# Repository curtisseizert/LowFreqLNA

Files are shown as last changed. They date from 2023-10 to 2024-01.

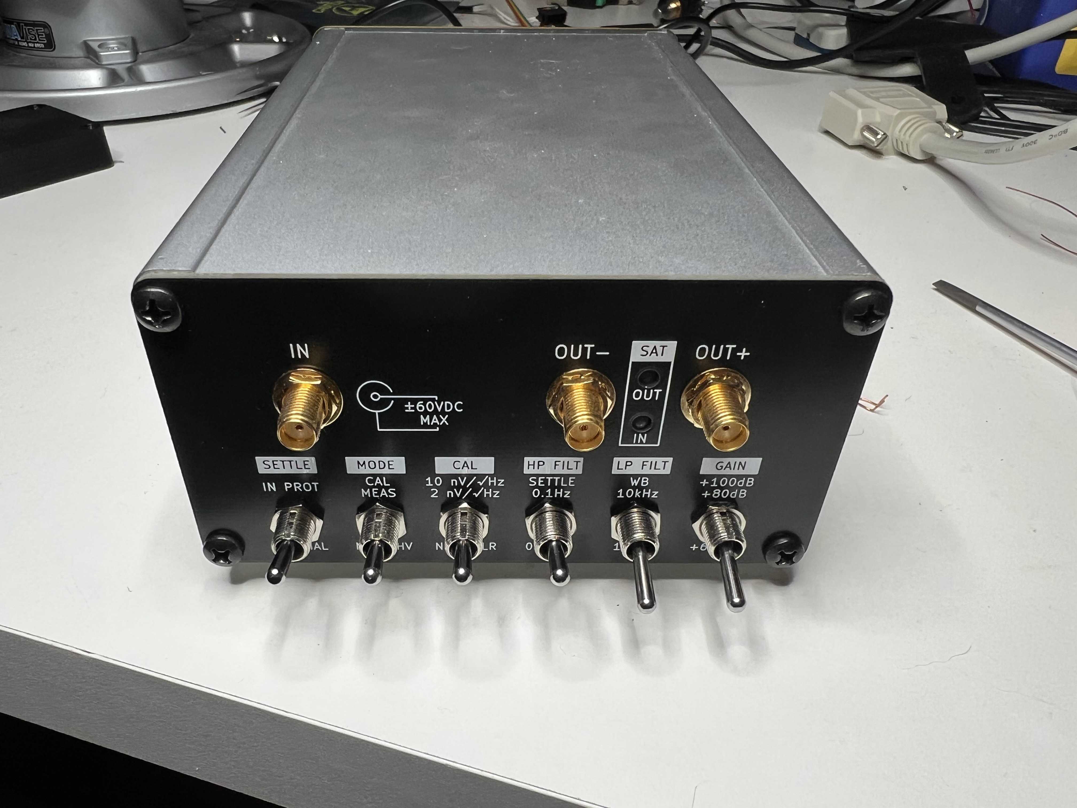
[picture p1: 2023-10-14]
Amplifier assembled.JPG

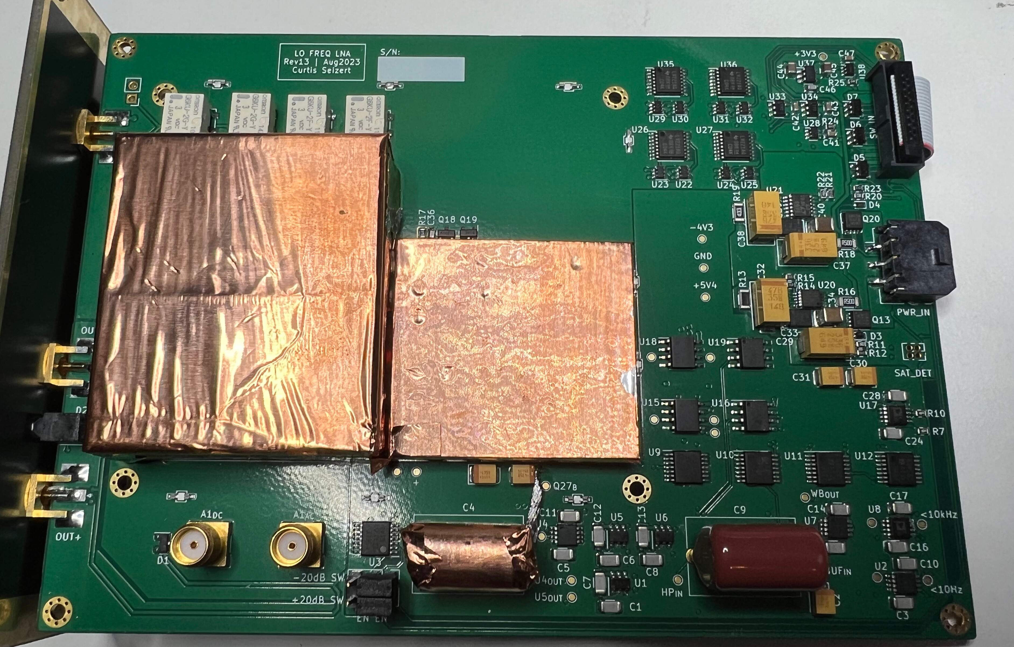
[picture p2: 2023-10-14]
Board top.jpg

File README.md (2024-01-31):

# LowFreqLNA
A 0.01Hz-1+MHz low noise amplifier

Amplifier assembled

Current Status
--------------
I have made two of these and have done a fair amount of testing to nail down root causes of some of the issues (see later in this readme) that have proven to be a bit of a nuisance. I am also moving things around a bit on the battery and battery charger boards to allow a board-to-board connection of the two and increase the clearance between the battery board and the amplifier board. I have also tested improvements to the input stage that significantly reduce the low frequency noise, lowering the 1/f corner to <1 Hz. These are detailed in the issues section #7.

1. Battery board revision: <b>complete</b>
2. Battery charger revision: <b>complete</b>
3. Low distortion buffer: back to drawing board
4. Main board revision: planning/schematic revision
5. BOM population: procrastinating

Introduction
------------

This repository contains the complete design files for a low noise AC coupled amplifier intended especially for characterization of 1/f noise of voltage references, DACs, etc. For broader applicability, it also has a reasonably high bandwidth of 2.5 MHz (measured, -3dB) at 60 or 80 dB gain, and about 1 MHz at 100 dB gain. Consistent with my primary use case for this amplifier, it has exceptionally low 1/f noise itself (measured at 3.2 nVRMS from 0.01-10 Hz) and a low broadband noise density of around 0.6 nV/rtHz. The quiescent current draw for the amplifier is about 30 mA, giving it a battery life of >100 h with the 4S 21700 Li batteries used to power the device. The project includes five PCBs:
(1) The main amplifier board
(2) The BMS board
(3) The SW board
(4) The front panel board
(5) The rear panel board/battery charger.

At present, I have hand assembled these using a converted toaster oven, which is a semi-onerous but doable-in-a-weekend task. As such, the BOMs are incomplete in all cases, which I will aim to rectify going forward. It is my hope that this will serve the needs of others designing voltage references, DACs, power supplies, etc. I may try to fix a couple things about this that have been bugging me, such as the lack of prefiltering and the antenna-like properties of the PP caps used in HP filters in the signal train. There is also a bit of room for reducing current draw. A fully differential version has been suggested, but if I work on that, I will make a separate repository for it.

The input stage is formed from a 24uF/100M RC high pass filter feeding a hybrid amplifier. The hybrid amplifier consists of 16 parallel JFE2140 dual JFETs in a cascode differential amplifier configuration. This drives an OPA140 op amp, which provides feedback via a 1k/2R divider to the inverting gate of the differential pair. The DC offset of the input stage is removed with a 2.2uF/10M HP filter. A switched gain stage amplifies the signal, which is HP filtered again to remove offsets and set the high-pass cutoff of the amplifier. The switched low-pass filtering is provided by two fourth-order butterworth filters in Sallen-Key topology. Switches select either one of these outputs or the unfiltered amplified signal to feed to the output stage.

A common problem with low-frequency AC coupled amplifiers is very long settling times when switching inputs. This is addressed with the "SETTLE" and "IN PROT" (Input protection) switches on the front panel. The former shorts the resistors of both of the post-input stage HP filter outputs with low-leakage MMBF4117 JFETs, and the latter shorts the input AC coupling filter by shorting the 100M resistor with a relay. The "IN PROT" switch also places a 6k04 resistor in series with the AC coupling filter to avoid large transients when switching between sources with different DC biases. With these switches, it is possible to take valid measurements down to 0.1 Hz with a minute or so of settling time and measurements down to 0.01 Hz with 5-10 minutes of settling time. Saturation of the amplifiers prior to both HP filters is detected with window comparators, which drive warning lights on the front panel. These features are meant to make it reasonably convenient to make low-level measurements and be confident the result is valid.

Electrical Characteristics
--------------------------

The following characteristics are taken from the one of these that I have fully assembled. Characterization was performed with a Digilent Analog Discovery Pro ADP3450 for bandwidths >10 kHz, a Keysight 34465A, and an HP3458A. Noise captures with the ADP3450 were digitized in Waveforms, exported, and transformed to the frequency domain using the SciPy Signal Python library in Spyder IDE. Captures with the HP3458A were taken using the PyVISA Python library for low frequency (50 SPS) digitization. The HP3458A was used for most low frequency work due to its superior isolation and common mode immunity. Bandwidth characterization was performed with the network analyzer utility in Waveforms for the ADP3450 and a 60dB attenuator. Gain calibration was performed by measuring the noise of a 6k04 resistor (9.97 nV/rtHz Johnson-Nyquist voltage noise density at 298k) comparing the bandwidth-limited RMS amplitude of the output signal to the theoretical value at the ambient temperature outside the amplifier. Linearity was checked by obtaining bandwidth-limited RMS amplitudes for a 240R resistor and a short, accounting for the RMS addition of the amplifier's own noise floor and that of the 240R resistor. The calibration resistors were 0.1%, 10 ppm/K thin film types. Quiescent current was measured by powering the amplifier with a Rigol DP832A DC power supply at +/-8V.

<table>
  <tr><td><b>Parameter</td><td><b>Condition</td><td><b>Result</td><td><b>Comment</td></tr>
  <tr><td>Voltage Noise Density</td><td>1 MHz</td><td>0.6 nV/rtHz</td><td>A</td></tr>
  <tr><td> </td><td>1 kHz</td><td>0.64 nV/rtHz</td><td>A</td></tr>
  <tr><td> </td><td>10 Hz</td><td>0.75 nV/rtHz</td><td>B</td></tr>
  <tr><td> </td><td>1 Hz</td><td>1.2 nV/rtHz</td><td>C</td></tr>
  <tr><td> </td><td>0.1 Hz</td><td>3.1 nV/rtHz</td><td>C</td></tr>
  <tr><td> </td><td>0.01 Hz</td><td>13.4 nV/rtHz</td><td>C,D</td></tr>
  <tr><td>Voltage Noise</td><td>0.1 Hz - 10 Hz</td><td>15 nV p-p</td><td>C</td></tr>
  <tr><td></td><td>0.01 Hz - 10 Hz</td><td>20 nV p-p</td><td>C</td></tr>
  <tr><td>Current Noise Density</td><td>0.1-1 Hz</td><td><2 fA/rtHz</td><td>E</td></tr>
  <tr><td>Input stage bias current</td><td></td><td>2.7 pA</td><td>F</td></tr>
  <tr><td>Input stage offset voltage</td><td></td><td>-94 uV</td><td>G</td></tr>
  <tr><td>-3dB Bandwidth</td><td>0R source impedance</td><td>2.8 MHz</td><td></td></tr>
  <tr><td>Input Capacitance</td><td>6k04 source impedance</td><td>140 pF</td><td>H</td></tr>
  <tr><td>10 kHz Low pass filter</td><td></td><td>4th order Butterworth</td><td></td></tr>
  <tr><td>10 Hz Low pass filter</td><td></td><td>4th order Butterworth</td><td></td></tr>
  <tr><td>THD</td><td>5 kHz</td><td><-70dB</td><td></td></tr>
  <tr><td>Quiescent Current</td><td>shorted input</td><td>30 mA</td><td></td></tr>
  <tr><td>Battery Capacity</td><td>Samsung 50S cells</td><td>5000 mA/h</td><td>nominal</td></tr>
  <tr><td>i_chg</td><td></td><td>2.7A</td><td></td></tr>
  <tr><td>Charger efficiency</td><td>V_Batt = 15V</td><td>98%</td><td>I</td></tr>
</table>

A: Full bandwidth, ADP-3450; B: 0.1-10 kHz bandwidth, ADP-3450; C: 0.01-10 Hz bandwidth, HP3458A; D: calc'd from measured value (9.5 nV/rtHz) and 3dB attenuation from HP filter; E: Calculated from open input VSD (100M resistor). Resulting noise was <0.1% from calculated value; F: Calculated from difference in offset voltage between 0R and 100M resistance to GND for input gate; G: Input gate shorted to GND; H: -3dB point with 6k04 resistor is 190 kHz. Primarily from board parasitics and RC damper; I: Measured on board, does not include cable losses

Spectra
-------

WB_Noisefloor
10kHz noisefloor loglog
10Hz noisefloor loglog
Calibration spectrum
0 1-10HzNoise
0 01-10HzNoise

Application: Measuring voltage noise of voltage references
----------------------------------------------------------
Due to the low noise floor of the preamplifier, it can be used to easily measure the voltage noise of even the quietest (room temperature) references without error due to its own noise floor. Additionally, the use of polypropylene AC coupling capacitors with low dielectric absorption and the inclusion of the "SETTLE" feature allow measurement down to 10 mHz without excessive settling time. The plot below shows the voltage noise spectral density of several ADR1000-based 10-V references. Due to the high input impedance at low frequency, increasing the source impedance does not measurably change the gain of the amplifier. This is not the case with common 1000 uF/1k AC-coupled LNAs, which give considerable gain errors at even moderate source impedances (e.g., a 100 Ohm source impedance would give a gain error of 9.1%).

ADR1000 selection VSDs

Issues
------

1. Input capacitance is higher than I'd like, which reduces the bandwidth with high impedance sources. Some of the capacitance is from board parasitics (ca. 100 pF), and some is from the R-C damper that is necessary to damp out oscillations with inductive sources (including most precision op amps). My plan to deal with this in the next revision is to modify the layout to reduce the board parasitics and switch in the R-C damper with an additional relay. Very little of the input capacitance is due to large Ciss of the paralleled JFETs as most of this presents as common mode capacitance and is bootstrapped by feedback. My target for input capacitance (with no R-C damper switched in) is 50 pF, but this is a lower priority than stability.
2. Second order (mostly) harmonic distortion of the ADA4622-2 buffer following the final HP filter stage leads to a DC offset term in the output. This is worst around 2 MHz and gets considerably worse with increasing ammplitude of the high frequency tone (it varies directly with the fourth power of the amplitude). The JFET switches are not a major issue (when SETTLE is off), which I have tested by removing them from the board. When SETTLE is on, it is worse, which negatively impacts settling time. As such, a 1 MHz sine wave amplitude modulated at 0.1 Hz will appear after 10 Hz LP filtering as a 0.1 Hz signal and harmonics, which is bad. The approach to this will be twofold: prefiltering and a composite buffer. Prefiltering will be described in #3. The composite buffer is a solution to a problem of a difficult convergence of design constraints: this buffer must have low Ib and current noise, reasonable common mode range (>+/-2.5V with 5.5V and -4.3V rails), low distortion at high frequency, and ability to operate on 10V total supply voltage with low quiescent current. To my knowledge, there are no monolithic amplifiers that satisfy these constraints. Without the high frequency distortion issue, only the ADA4622, OPAx191, and OPAx192 were good choices to my knowledge, but all of these led to the distortion-induced offset issue. In simulation, a dual JFET follower feeding an ADA4805 does well with a total quiescent current of about 1.1 mA and <0.1 dB peaking. I will prototype this block and test it before committing to the design for the next revision.
3. Amplifying signals at full bandwidth limits dynamic range for LF noise analyses. I will address this by filtering prior to the final gain stages, probably with a single-pole RC filter. Another solution would be to have the LP filter stages operate at gain >1, but I would prefer not to take this tack because it would mean the gain error of the amplifier is dependent on which LP filter stage is switched in.
4. Input protection switching is inconsistent due to contact bounce. I did not think this would be an issue with the one-shots used for relay switching, but it is. For now, connecting the K1_SW signal to both GND and 3V3 with 22k resistors does the trick, but this is not ideal, so I will implement a more robust dual-inverter debounce block for all the relay switches. In practice, however, only K1 seems to be affected by this issue due to it being switched differently on the front panel.
5. The 0804 (4x0402) resistor arrays are a PITA and almost always need to be fixed after reflow, so I'll replace those with 1206 (4x0603) arrays.
6. The 2.2 uF PP caps used in the HP filters seem to radiate, which requires shielding the input HP filter caps (these need to be PP for leakage). This shielding increases input capacitance (to ground), so I will replace the 2.2 uF caps with a few paralleled 470nF C0G capacitors, which have sufficiently low leakage to nullify the modest DC offsets following each stage, even with low frequency breakpoints.
7. The low frequency noise of the input stage is negatively impacted by the current noise of the mirror transistors. The fact that the low frequency noise is sub-optimal is evident from low frequency noise measurements of a pair of JFE2140s configured as source followers biased to the same drain current as a pair in the input stage. Because there are 16 such pairs in the LNA, the ratio of the NSD curves for this DUT and the noise floor should give a flat SNR of 12 dB, but this was not the case in the current revision. The most likely culprits to investigate were current noise from the NPN cascode transistor pair and current noise from the PNP current mirror transistor pair. Tests of the low frequency current noise of the NPN pair showed it was an unlikely culprit, accounting for perhaps 2% of the noise density at 10 mHz. Deletion of the current mirror pair, however, resolved the issue without any ill effects. This part was superfluous because the load seen by the collectors of the NPN cascode pair is the current mirror (or resistive loads) in parallel with 1/gm of the PNP folded cascode pair. With a collector current of ca. 100 uA, 1/gm is about 250R. With 330R resistive loads (i.e., shorting the collectors and emitters of the mirror transistors), the load drops from ~250R to ~142R, which still allows sufficiently high voltage gain at the emitters of the PNP pair to ensure they do not add significant noise. The effect of this modification on the low frequency noise is shown below.

JFE2140 Noise test setup

Current mirror effect on NSD

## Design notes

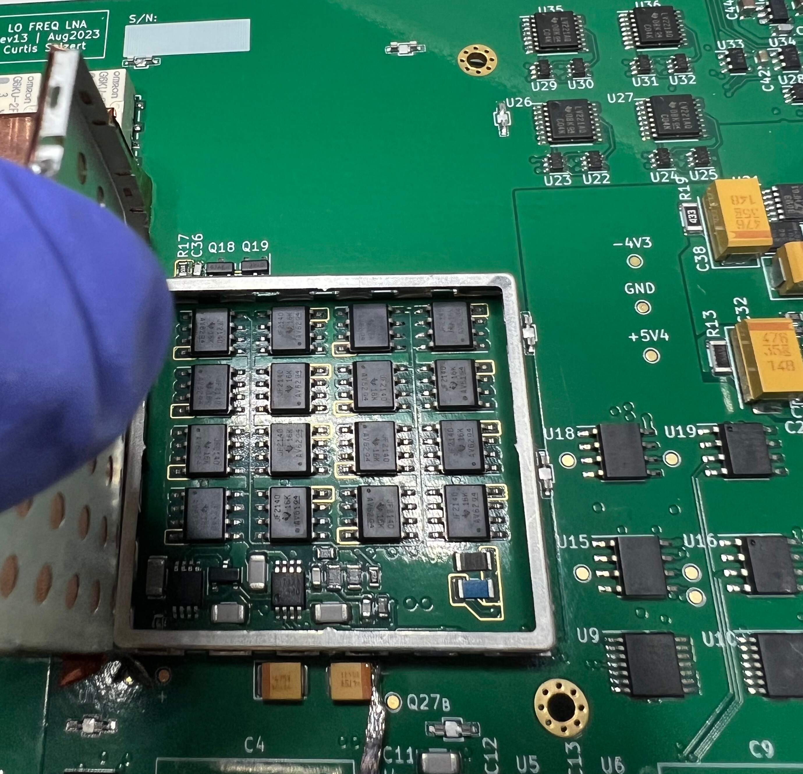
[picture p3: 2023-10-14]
Input stage.jpg

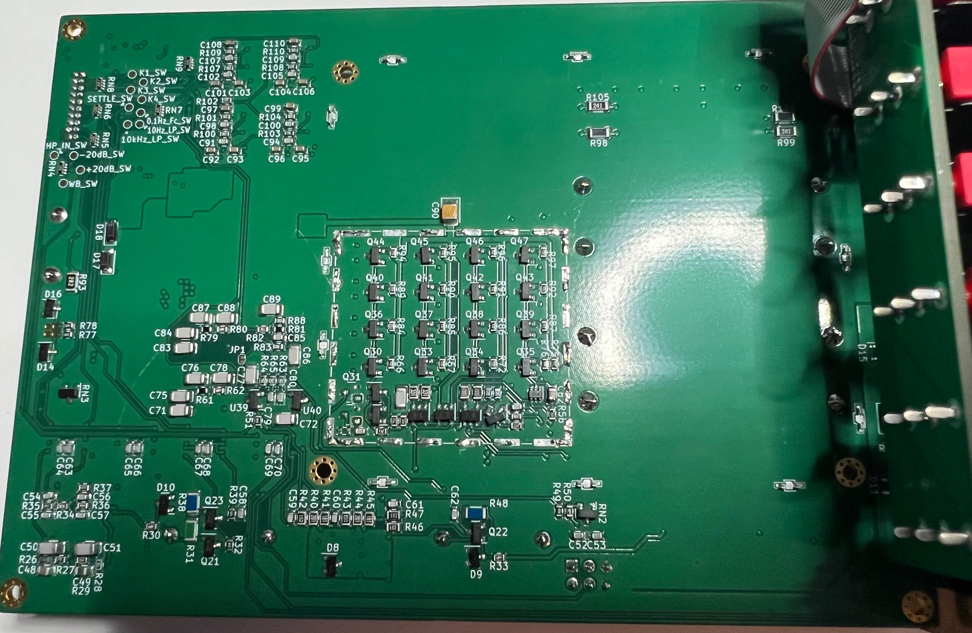
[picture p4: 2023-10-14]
Board bottom.jpg

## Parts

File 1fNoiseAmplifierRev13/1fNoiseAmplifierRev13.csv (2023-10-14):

Source: | C:\Users\Curtis\Documents\KiCAD\1fNoiseAmp\1fNoiseAmpRev12\1fNoiseAmpRev12.kicad_sch
Date: | 7/12/2023 12:35:11 AM
Tool: | Eeschema (6.0.11)
Generator: | C:\Program Files\KiCad\6.0\bin\scripting\plugins/bom_csv_grouped_by_value_with_fp.py
Component Count: | 376
Ref | Qnty | Value | Cmp name | Footprint | Description | Vendor
C1, C2, C3, C4, C5, C6, C7, C8, C11, C12, C13, C14, C16, C17, C18, C19, C20, C21, C66, C67, C84, | 21 | 100nF | C_Small | Capacitor_SMD:C_1206_3216Metric_Red | Unpolarized capacitor, small symbol
C9, C10, C15, C91, C92, | 5 | 47uF/16V | CP1_Small | Capacitor_Tantalum_SMD:CP_EIA-3528-12_Kemet-T | Polarized capacitor, small US symbol
C22, C23, C25, C26, C94, | 5 | 100nF X7R | C_Small | Capacitor_SMD:C_0603_1608Metric_red_outline | Unpolarized capacitor, small symbol
C24, C27, C28, C29, C30, C31, C32, C33, C34, C35, C36, C37, C38, C39, C40, C41, C42, C43, C44, C45, C46, C48, C49, C51, C52, C57, C64, C85, | 28 | 10nF | C_Small | Capacitor_SMD:C_0603_1608Metric_red_outline | Unpolarized capacitor, small symbol
C47, C63, | 2 | 10x470nF | C_Small | Capacitor_SMD:C_1206x10_3216Metric_Red | Unpolarized capacitor, small symbol
C50, | 1 | 33pF | C_Small | Capacitor_SMD:C_0603_1608Metric_red_outline | Unpolarized capacitor, small symbol | 81-GRM185C1H330GA01J
C53, C54, | 2 | 10pF C0G | C_Small | Capacitor_SMD:C_0603_1608Metric_red_outline | Unpolarized capacitor, small symbol
C55, C61, | 2 | 1nF | C_Small | Capacitor_SMD:C_0603_1608Metric_red_outline | Unpolarized capacitor, small symbol
C56, C62, | 2 | 47nF | C_Small | Capacitor_SMD:C_0805_2012Metric_Red_outline | Unpolarized capacitor, small symbol
C58, C65, | 2 | 470nF | C_Small | Capacitor_SMD:C_1206_3216Metric_Red | Unpolarized capacitor, small symbol
C59, C60, C78, | 3 | 10nF C0G | C_Small | Capacitor_SMD:C_0603_1608Metric_red_outline | Unpolarized capacitor, small symbol
C68, C69, | 2 | 10uF/25V | CP1_Small | Capacitor_Tantalum_SMD:CP_EIA-3528-12_Kemet-T | Polarized capacitor, small US symbol
C70, C71, | 2 | 33uF/25V | CP1_Small | Capacitor_Tantalum_SMD:CP_EIA-7343-31_Kemet-D | Polarized capacitor, small US symbol
C72, C73, | 2 | 10uF/35V | C_Small | Capacitor_SMD:C_1210_3225Metric | Unpolarized capacitor, small symbol
C74, C80, | 2 | 2.2uF X7R | C_Small | Capacitor_SMD:C_0805_2012Metric_Red_outline | Unpolarized capacitor, small symbol
C75, C76, | 2 | 22uF/50V | CP1_Small | Capacitor_Tantalum_SMD:CP_EIA-7343-31_Kemet-D | Polarized capacitor, small US symbol
C77, C79, | 2 | 10uF/25V | CP1_Small_Kelvin | Capacitor_Tantalum_SMD:CP_EIA-3528-12_Kemet-T_Kelvin | Polarized capacitor, small US symbol
C81, | 1 | 63x470nF/25V | C_Small | Capacitor_SMD:C_1206_Parallel | Unpolarized capacitor, small symbol
C82, | 1 | DNP | C_Small | Resistor_SMD:R_0603_1608Metric_red | Unpolarized capacitor, small symbol
C83, | 1 | 47nF/25V | C_Small | Capacitor_SMD:C_0805_2012Metric_Red_outline | Unpolarized capacitor, small symbol
C86, | 1 | 3.3pF C0G | C_Small | Capacitor_SMD:C_0603_1608Metric_red_outline | Unpolarized capacitor, small symbol | 81-GCM1885C2A3R3BA6D
C87, C88, C89, C90, | 4 | 100nF/50V | C_Small | Capacitor_SMD:C_1206_3216Metric_Red | Unpolarized capacitor, small symbol
C93, | 1 | 68pF C0G | C_Small | Capacitor_SMD:C_0603_1608Metric_red_outline | Unpolarized capacitor, small symbol | 81-GCM1885C2A680FA6D
D1, D2, D3, | 3 | ESDA6V1-5SC6 | ESDA6V1-5SC6 | Package_TO_SOT_SMD:SOT-23-6 | Quintuple bidirectional transil, Suppressor for ESD protection, 6V1 Breakdown, SOT-23-6
D4, D5, D6, D7, D8, D9, D10, D11, D19, D20, | 10 | DZ2S100X0L | DZ2S100X0L | Diode_SMD:D_SOD-523 | 150mW Silicon Planar Zener Diode, 10V, SOD-523 | 755-EDZVFHT2R10B
D12, D13, D14, D15, D17, D18, D22, D25, | 8 | BAV199 | BAV99 | Package_TO_SOT_SMD:SOT-23 | BAV99 High-speed switching diodes, SOT-23
D16, | 1 | LED | LED | LED_SMD:LED_Dialight_591 | Light emitting diode
D21, | 1 | BAV199DW | BAV199DW | Package_TO_SOT_SMD:SOT-363_SC-70-6 | Quad Surface Mount Low Leakage Diode, SOT-363
D23, D24, | 2 | MBR0540 | MBR0540 | Diode_SMD:D_SOD-123 | 40V 0.5A Schottky Power Rectifier Diode, SOD-123
H1, H2, H3, H4, | 4 | MountingHole_Pad | MountingHole_Pad | MountingHole:MountingHole_2.2mm_M2_Pad_Via | Mounting Hole with connection
J1, | 1 | Conn_Coaxial | Conn_Coaxial | Connector_Coaxial:SMA_Molex_73251-2120_EdgeMount_Horizontal | coaxial connector (BNC, SMA, SMB, SMC, Cinch/RCA, LEMO, ...)
J2, | 1 | Conn_01x02 | Conn_01x02 | Connector_PinHeader_2.54mm:PinHeader_1x02_P2.54mm_Vertical | Generic connector, single row, 01x02, script generated (kicad-library-utils/schlib/autogen/connector/)
J3, | 1 | IDC_HDR | Conn_02x10_Odd_Even | Connector_PinHeader_1.27mm:PinHeader_2x10_P1.27mm_Vertical | Generic connector, double row, 02x10, odd/even pin numbering scheme (row 1 odd numbers, row 2 even numbers), script generated (kicad-library-utils/schlib/autogen/connector/)
J4, | 1 | PIN_JMP | Conn_02x03_Odd_Even | Connector_PinHeader_2.54mm:PinHeader_2x03_P2.54mm_Vertical | Generic connector, double row, 02x03, odd/even pin numbering scheme (row 1 odd numbers, row 2 even numbers), script generated (kicad-library-utils/schlib/autogen/connector/)
J5, J23, | 2 | Conn_Coaxial | Conn_Coaxial | Connector_Coaxial:SMA_Molex_73251-135_SMT_Vertical | coaxial connector (BNC, SMA, SMB, SMC, Cinch/RCA, LEMO, ...)
J6, J7, J8, J9, J10, J11, J12, J13, J14, J15, J16, J17, | 12 | ShieldClip | Conn_01x01 | RF_Shielding:RF_Shield_Clip_Harwin_Mini | Generic connector, single row, 01x01, script generated (kicad-library-utils/schlib/autogen/connector/)
J18, J19, | 2 | RF_Shield_Two_Pieces | RF_Shield_Two_Pieces | RF_Shielding:Laird_Technologies_BMI-S-230-F_50.8x38.1mm | Two-piece EMI RF shielding cabinet | 739-BMI-S-230-F
J20, J21, | 2 | SMA_OUT | Conn_Coaxial | Connector_Coaxial:SMA_Molex_73251-2120_EdgeMount_Horizontal | coaxial connector (BNC, SMA, SMB, SMC, Cinch/RCA, LEMO, ...)
J22, | 1 | Micro-Fit 3.0 43650-0310 | Conn_01x03_MountingPin | Connector_Molex:Molex_Micro-Fit_3.0_43650-0310_1x03-1MP_P3.00mm_Horizontal_PnP | Generic connectable mounting pin connector, single row, 01x03, script generated (kicad-library-utils/schlib/autogen/connector/) | 538-43650-0310
K1, K2, K3, K4, | 4 | G6KU-2 | G6KU-2 | Relay_SMD:Relay_DPDT_Omron_G6K-2G-Y | Miniature 2-pole relay, Single-winding Latching | 653-G6KU-2G-Y-DC5
Q1, Q3, Q5, Q7, Q22, | 5 | BSS84 | BSS84 | Package_TO_SOT_SMD:SOT-23 | -0.13A Id, -50V Vds, P-Channel MOSFET, SOT-23
Q2, Q4, Q6, Q8, | 4 | BSS123 | BSS123 | Package_TO_SOT_SMD:SOT-23 | 0.17A Id, 100V Vds, N-Channel MOSFET, SOT-23
Q9, Q10, Q11, Q14, Q15, | 5 | MMBF4117 | MMBF4117 | Package_TO_SOT_SMD:SOT-23 | Low leakage N-Channel JFET, SOT-23
Q12, | 1 | SiS443DN | SiS443DN | Package_SO:Vishay_PowerPAK_1212-8_Single | -35A Id, -40V Vds, P-Channel MOSFET, PowerPAK 1212-8 Single
Q13, | 1 | SiS862ADN | SiS862ADN | Package_SO:Vishay_PowerPAK_1212-8_Single | 52A Id, 60V Vds, 7.2mOhm Rds(ON), N-Channel MOSFET, PowerPAK 1212-8 Single
Q16, Q17, Q20, Q24, Q27, Q29, Q31, Q33, Q35, Q37, Q39, Q41, Q43, Q45, Q47, Q49, Q51, Q53, | 18 | MMBT3904 | MMBT3904 | Package_TO_SOT_SMD:SOT-23 | 0.2A Ic, 40V Vce, Small Signal NPN Transistor, SOT-23
Q18, Q23, Q26, Q28, Q30, Q32, Q34, Q36, Q38, Q40, Q42, Q44, Q46, Q48, Q50, Q52, | 16 | JFE2140 | JFE2140 | Package_SO:SOIC-8_3.9x4.9mm_P1.27mm | Ultra-low Noise, Matched, Dual, Low-Gate Current, Discrete Audio N-Channel JFET
Q19, | 1 | HN4C51J | HN4C51J | Package_TO_SOT_SMD:SOT-23-5_red | 120V 100mA Common Base Audio Frequency GP NPN Pair
Q21, Q25, | 2 | HN4A51J | HN4A51J | Package_TO_SOT_SMD:SOT-23-5_red | 120V 100mA Common Base Audio Frequency GP PNP Pair
R1, | 1 | 6k02 0.1% | R_US | Resistor_SMD:R_1206_3216Metric_red | Resistor, US symbol | 667-ERA-8AEB6041V
R2, | 1 | 240R 0.1% | R_US | Resistor_SMD:R_1206_3216Metric_red | Resistor, US symbol | 667-ERA-8AEB241V
R3, R67, R68, | 3 | 0R5 | R_US | Resistor_SMD:R_1206_3216Metric_red | Resistor, US symbol
R4, R5, R6, R7, R8, R9, R12, R13, R14, R15, R58, | 11 | 10k | R_US | Resistor_SMD:R_0603_1608Metric_red | Resistor, US symbol
R10, R11, R16, R17, R18, R19, R20, R21, R22, R23, R63, R64, R90, R91, | 14 | 1M | R_US | Resistor_SMD:R_0603_1608Metric_red | Resistor, US symbol
R24, R25, R54, R55, R56, R59, R60, R100, R111, | 9 | 49R9 | R_US | Resistor_SMD:R_0603_1608Metric_red | Resistor, US symbol
R26, | 1 | 10M | R_US | Resistor_SMD:R_1206_3216Metric_red | Resistor, US symbol
R27, R28, R103, | 3 | 1k 0.1% | R_US | Resistor_SMD:R_0805_2012Metric_red | Resistor, US symbol
R29, | 1 | 49R9 0.1% | R_US | Resistor_SMD:R_0805_2012Metric_red | Resistor, US symbol
R30, R31, R49, R51, R86, | 5 | 1k | R_US | Resistor_SMD:R_0603_1608Metric_red | Resistor, US symbol
R32, | 1 | 47R5 | R_US | Resistor_SMD:R_0805_2012Metric_red | Resistor, US symbol | 667-ERA-6AEB47R5V
R33, | 1 | 1k24 0.1% | R_US | Resistor_SMD:R_0805_2012Metric_red | Resistor, US symbol | 71-TNPW08051K24BEEA
R34, | 1 | 240R 0.1% | R_US | Resistor_SMD:R_0805_2012Metric_red | Resistor, US symbol | 754-RG2012N-241-WT1
R35, | 1 | 220R | R_US | Resistor_SMD:R_0805_2012Metric_red | Resistor, US symbol | 667-ERA-6VEB2200V
R36, | 1 | 2k67 | R_US | Resistor_SMD:R_0603_1608Metric_red | Resistor, US symbol | 754-RR0816P-2671D42H
R37, | 1 | 56k2 | R_US | Resistor_SMD:R_0603_1608Metric_red | Resistor, US symbol | 754-RR0816P-5622D73C
R38, | 1 | 2k4 0.1% | R_US | Resistor_SMD:R_0805_2012Metric_red | Resistor, US symbol | 667-ERA-6ARW242V
R39, | 1 | 9k53 | R_US | Resistor_SMD:R_0603_1608Metric_red | Resistor, US symbol
R40, R84, | 2 | 200k | R_US | Resistor_SMD:R_0603_1608Metric_red | Resistor, US symbol | 754-RR0816P-204D
R41, | 1 | 2M87 | R_US | Resistor_SMD:R_0603_1608Metric_red | Resistor, US symbol
R42, R43, | 2 | 2M49 | R_US | Resistor_SMD:R_0603_1608Metric_red | Resistor, US symbol | 603-RC0603FR-072M49L
R44, | 1 | 1M8 | R_US | Resistor_SMD:R_0603_1608Metric_red | Resistor, US symbol | 603-AC0603FR-071M8L
R45, R97, | 2 | 887R | R_US | Resistor_SMD:R_0603_1608Metric_red | Resistor, US symbol | 754-RR0816P-8870D92A
R46, | 1 | 18k7 | R_US | Resistor_SMD:R_0603_1608Metric_red | Resistor, US symbol | 754-RR0816P-1872D27C
R47, R76, R77, R82, | 4 | 28k7 | R_US | Resistor_SMD:R_0603_1608Metric_red | Resistor, US symbol
R48, | 1 | 604k | R_US | Resistor_SMD:R_0603_1608Metric_red | Resistor, US symbol | 603-RT0603DRE07604KL
R50, R61, R62, | 3 | 100k | R_US | Resistor_SMD:R_0603_1608Metric_red | Resistor, US symbol
R52, | 1 | 499k | R_US | Resistor_SMD:R_1206_3216Metric_red | Resistor, US symbol | 667-ERA-8AEB4993V
R53, | 1 | 4M7 | R_US | Resistor_SMD:R_1206_3216Metric_red | Resistor, US symbol | 594-MCA1206MD4704BP1
R57, | 1 | 10M | R_US | Resistor_SMD:R_0603_1608Metric_red | Resistor, US symbol
R65, R66, | 2 | 2R | R_US | Resistor_SMD:R_0603_1608Metric_red | Resistor, US symbol
R69, | 1 | 43k 0.1% | R_US | Resistor_SMD:R_1206_3216Metric_red | Resistor, US symbol | 667-ERA-8AEB433V
R70, | 1 | 53k6 | R_US | Resistor_SMD:R_1206_3216Metric_red | Resistor, US symbol | 667-ERA-8AEB53R6V
R71, | 1 | 499k | R_US | Resistor_SMD:R_0603_1608Metric_red | Resistor, US symbol
R72, R74, | 2 | 30k1 | R_US | Resistor_SMD:R_0603_1608Metric_red | Resistor, US symbol
R73, | 1 | 360k | R_US | Resistor_SMD:R_0603_1608Metric_red | Resistor, US symbol | 754-RR0816P-364D
R75, | 1 | 100M | R_US | Resistor_SMD:R_1206_3216Metric_red | Resistor, US symbol | 708-HVCB1206FKC100M
R78, | 1 | 7k5 | R_US | Resistor_SMD:R_0603_1608Metric_red | Resistor, US symbol | 754-RR0816P-752D
R79, R81, R85, R89, R92, R94, R95, R96, R98, R99, R102, R105, R106, R107, R108, R109, R110, | 17 | 3k3 | R_US | Resistor_SMD:R_0603_1608Metric_red | Resistor, US symbol | 754-RR0816P-332D
R80, R83, | 2 | 330 0.1% | R_US | Resistor_SMD:R_0805_2012Metric_red | Resistor, US symbol
R87, R88, | 2 | 33k 0.1% | R_US | Resistor_SMD:R_0805_2012Metric_red | Resistor, US symbol
R93, | 1 | 100R | R_US | Resistor_SMD:R_0603_1608Metric_red | Resistor, US symbol
R101, | 1 | 4R7 | R_US | Resistor_SMD:R_0603_1608Metric_red | Resistor, US symbol | 603-RT0603FRE074R7L
R104, | 1 | 4R99 0.1% | R_US | Resistor_SMD:R_0805_2012Metric_red | Resistor, US symbol
RN1, RN2, RN3, | 3 | 33R | R_Pack04 | Resistor_SMD:R_Array_Convex_4x0402 | 4 resistor network, parallel topology
RN4, | 1 | 9k/1k | Voltage_Divider | Package_TO_SOT_SMD:SOT-23 | Voltage divider | 71-MPMT10019001AT1
RN5, RN6, | 2 | 10k/10k | Voltage_Divider | Package_TO_SOT_SMD:SOT-23 | Voltage divider
RN7, RN8, RN9, | 3 | 1M | R_Pack04 | Resistor_SMD:R_Array_Convex_4x0402 | 4 resistor network, parallel topology
TP1, TP2, TP3, TP4, TP5, TP6, TP7, TP8, TP9, TP10, TP11, TP12, TP13, TP14, TP15, TP16, TP17, TP18, TP19, TP20, TP21, TP22, TP23, TP24, TP25, TP26, TP27, TP28, TP29, TP30, TP31, | 31 | TestPoint | TestPoint | TestPoint:TestPoint_Pad_D1.0mm | test point
U1, U2, U4, | 3 | TLV1812D | TLV1812D | Package_SO:SOIC-8_3.9x4.9mm_P1.27mm | Dual Rail-to-Rail Input Comparators with Push-Pull Output, SOIC-8
U3, U7, U12, U15, U16, | 5 | DG636EEQ | DG636EEQ_4 | Package_SO:TSSOP-14_4.4x5mm_P0.65mm | 0.3 pC Charge Injection, 100 pA Leakage
U5, U21, | 2 | OPA140 | OPA140 | Package_SO:MSOP-8_3x3mm_P0.65mm | High-Precision, Low-Noise, RRO, 11 MHz JFET Op Amp
U6, U8, U10, U11, U20, | 5 | ADA4622-2 | OPA2145 | Package_SO:MSOP-8_3x3mm_P0.65mm | Dual Operational Amplifiers, DIP-8/SOIC-8/TSSOP-8/VSSOP-8
U9, U13, | 2 | ADA4807-1 | ADA4807-1 | Package_TO_SOT_SMD:SOT-23-6_red | Single Rail-to-Rail Input/Output Amplifiers, with disable, SC-70-6/SOT-23-6
U14, | 1 | TLC555xD | TLC555xD | Package_SO:SOIC-8_3.9x4.9mm_P1.27mm | Single LinCMOS Timer, 555 compatible, SOIC-8 | 700-ICM7555ISAT
U17, | 1 | LT3042xMSE | LT3042xMSE | Package_SO:MSOP-10EP-3x3_P0.5mm_EP_thermal_vias_opt | 200mA, Adjustable, Ultralow Noise, Ultrahigh PSRR RF Linear Regulator, MSOP-10
U18, | 1 | LP2985-3.3 | LP2985-3.3 | Package_TO_SOT_SMD:SOT-23-5 | 150mA 16V Low-noise Low-dropout Regulator With Shutdown, 3.3V output voltage, SOT-23-5
U19, | 1 | LT3093xMSE | LT3093xMSE | Package_SO:MSOP-12-1EP_3x4mm_P0.65mm_EP1.65x2.85mm_ThermalVias_opt | -200mA, Adjustable, Ultralow Noise, Ultrahigh PSRR RF Negative Linear Regulator, MSOP-12
U22, | 1 | 74AUP1G02 | 74AUP1G02 | Package_TO_SOT_SMD:SOT-353_SC-70-5 | Single NOR Gate, Low-Voltage CMOS | 595-SN74AUP1G02DCKT

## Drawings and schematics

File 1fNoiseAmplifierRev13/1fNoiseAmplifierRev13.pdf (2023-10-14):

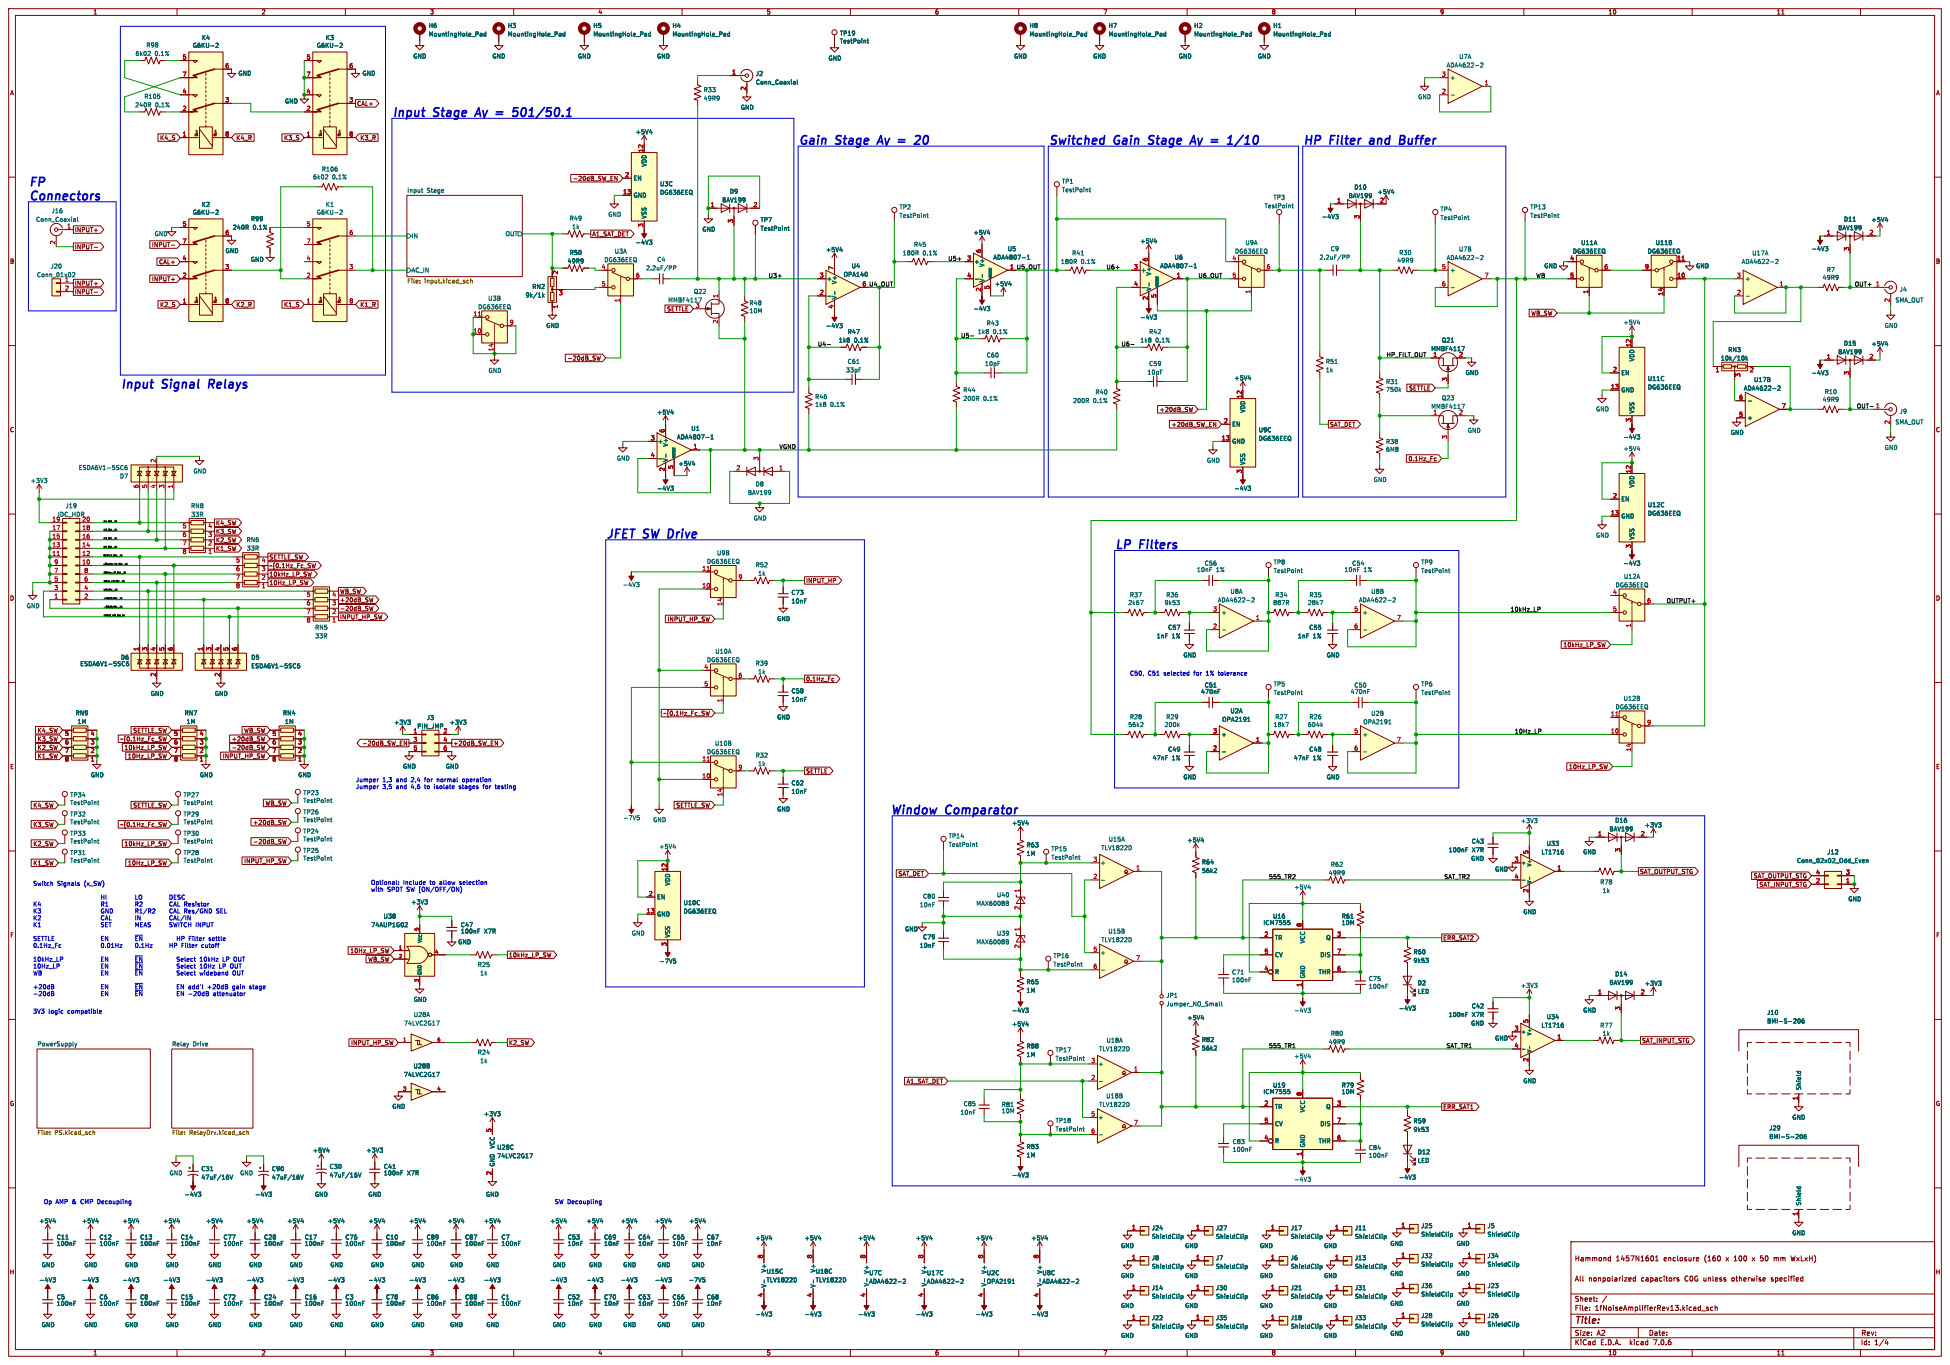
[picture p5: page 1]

HP Filter and Buffer

TP27 TestPoint TP30 TestPoint TP29 TestPoint TP28 TestPoint GND

Jumper 1,3 and 2,4 for normal operation

Jumper 3,5 and 4,6 to isolate stages for testing Switch Signals (x_SW) HI LO DESC

Op AMP & CMP Decoupling

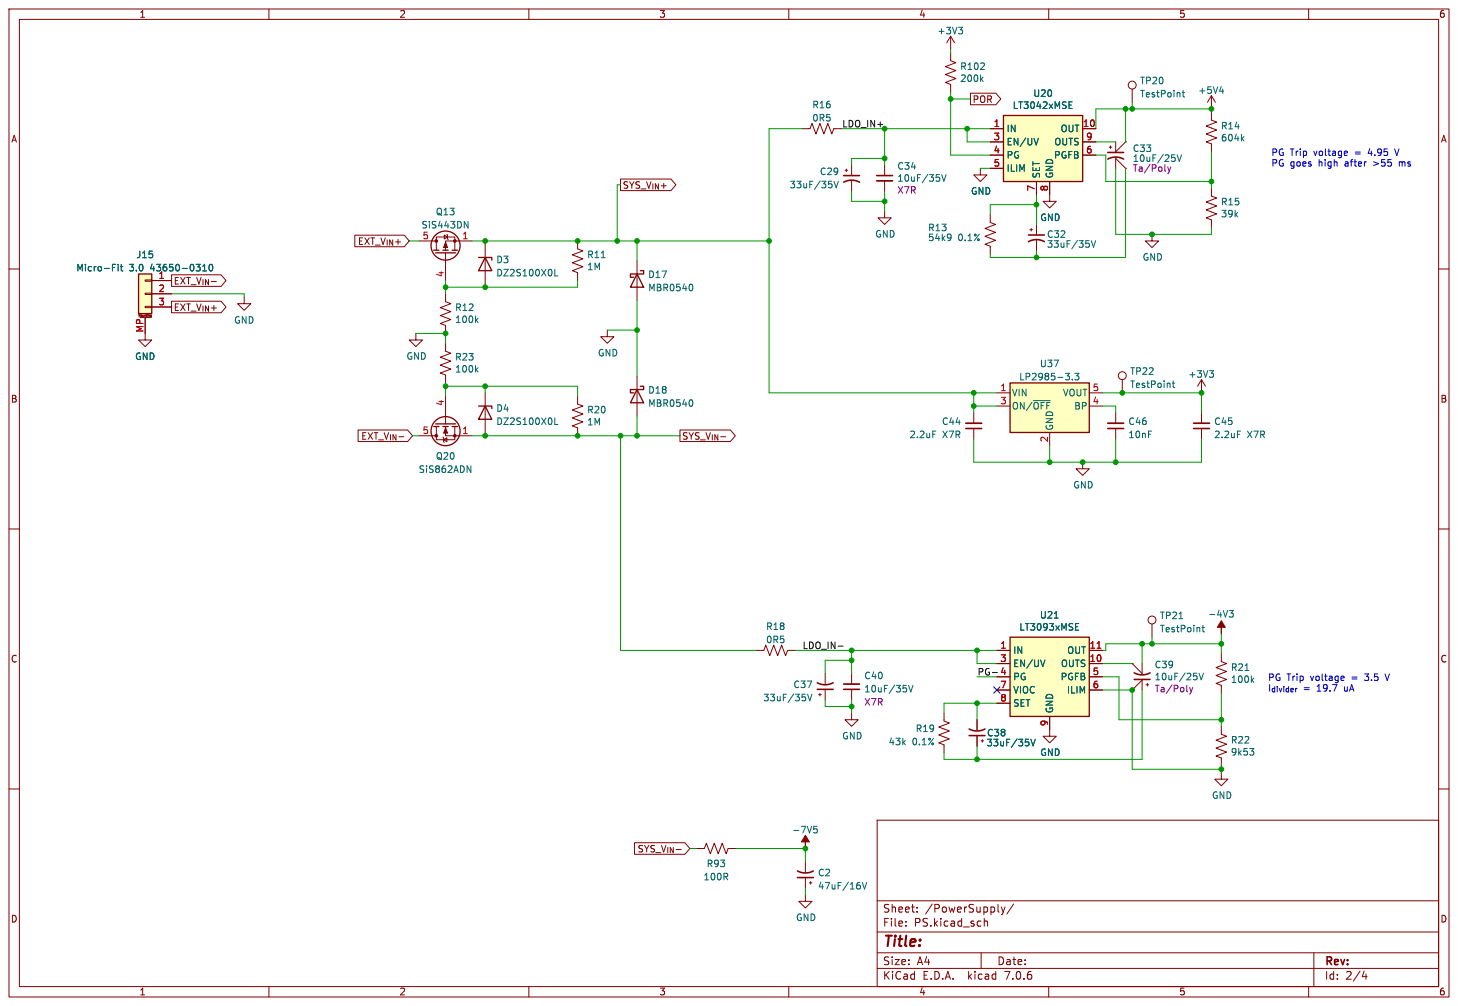
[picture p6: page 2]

PG goes high after >55 ms PG Trip voltage = 3.5 V

2 ON/~{OFF} 3 BP 4 VOUT 5 U37

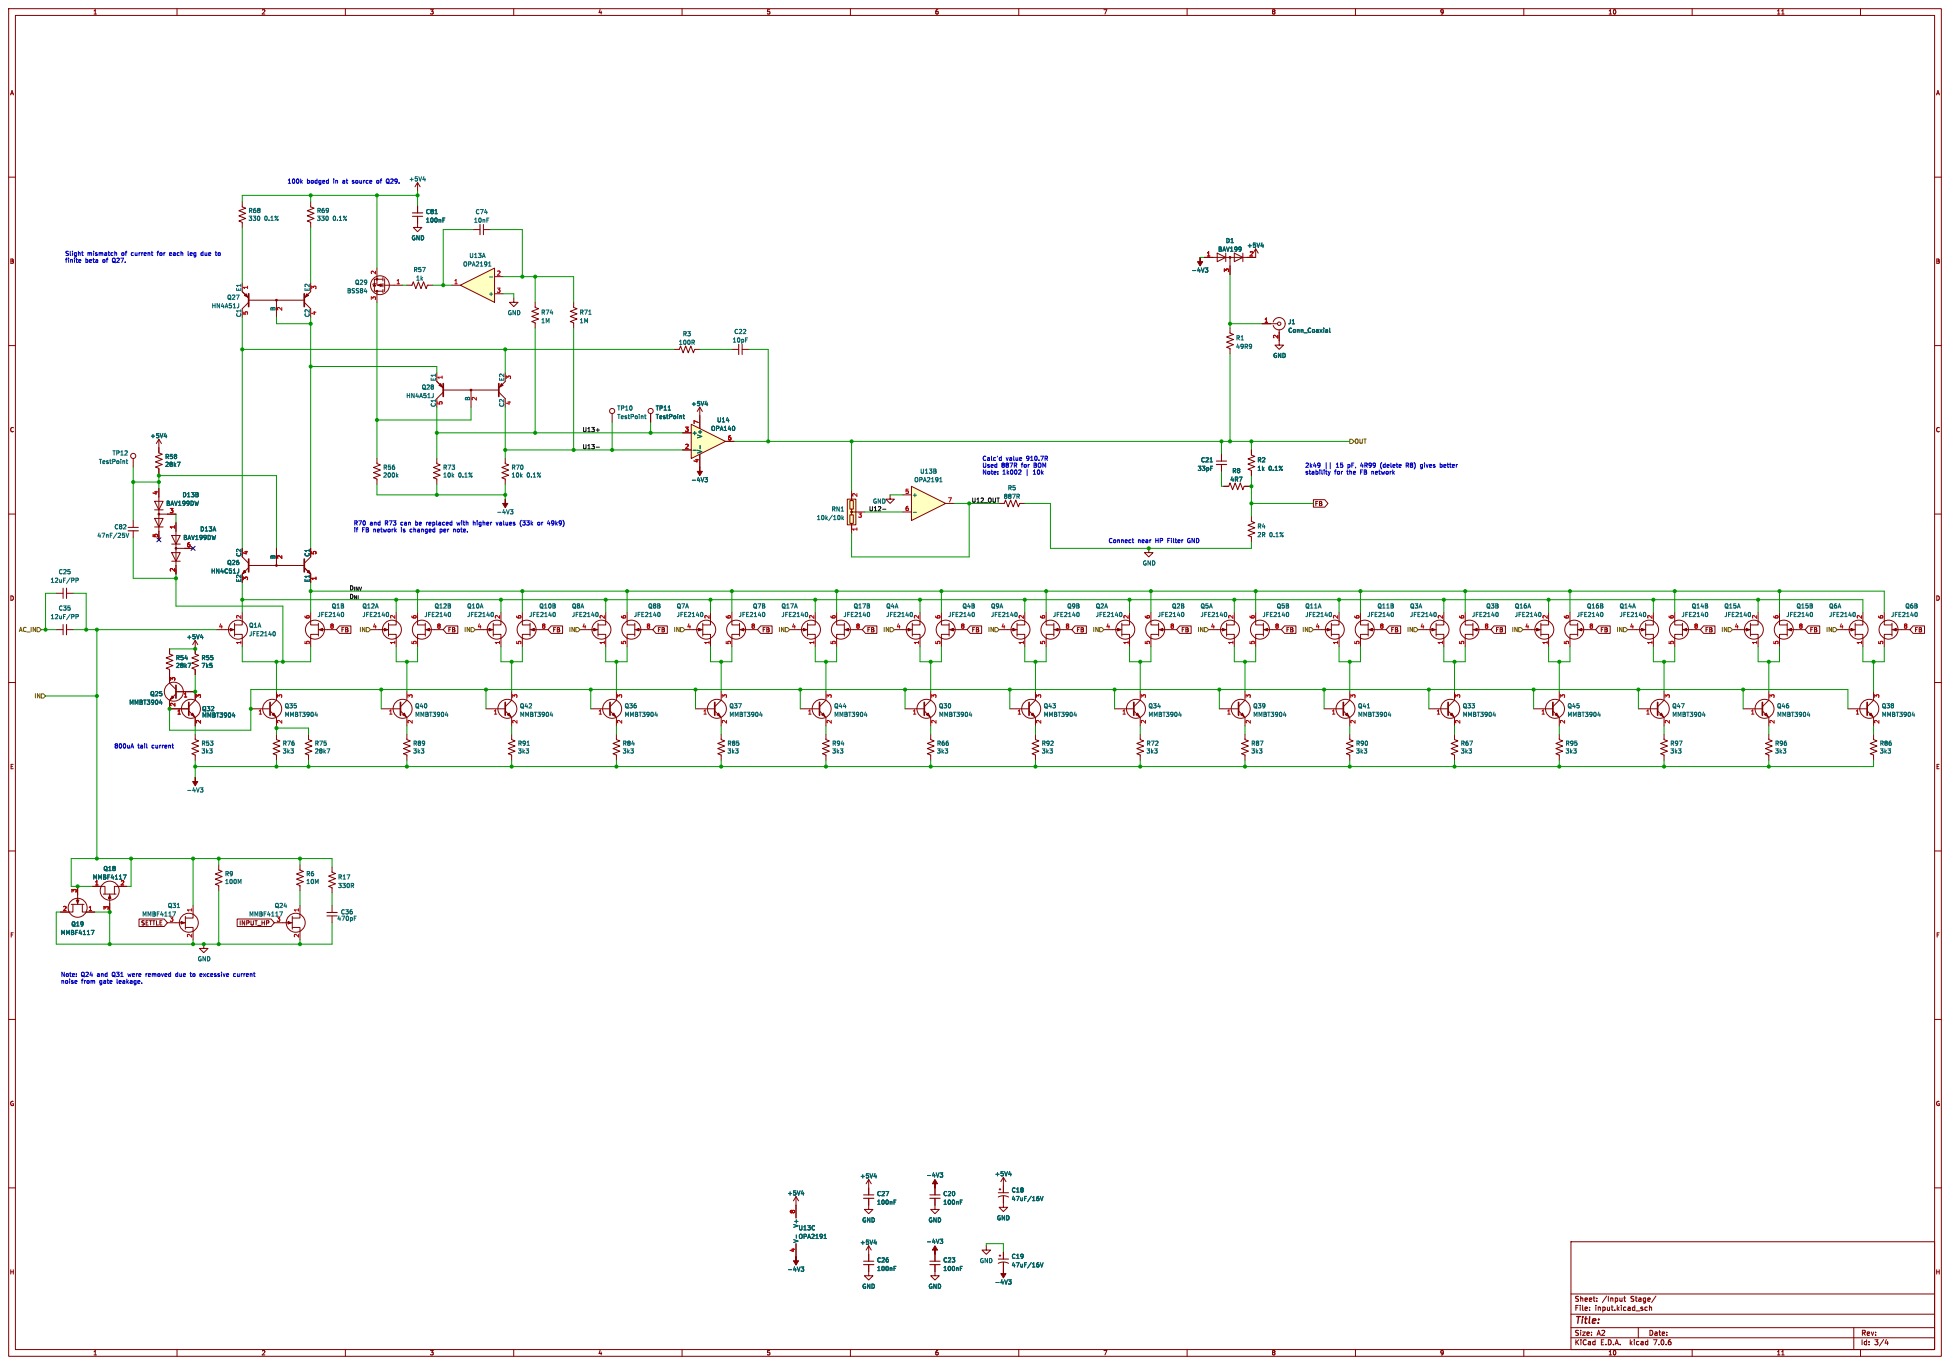
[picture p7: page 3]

if FB network is changed per note. 800uA tail current Note: Q24 and Q31 were removed due to excessive current noise from gate leakage.

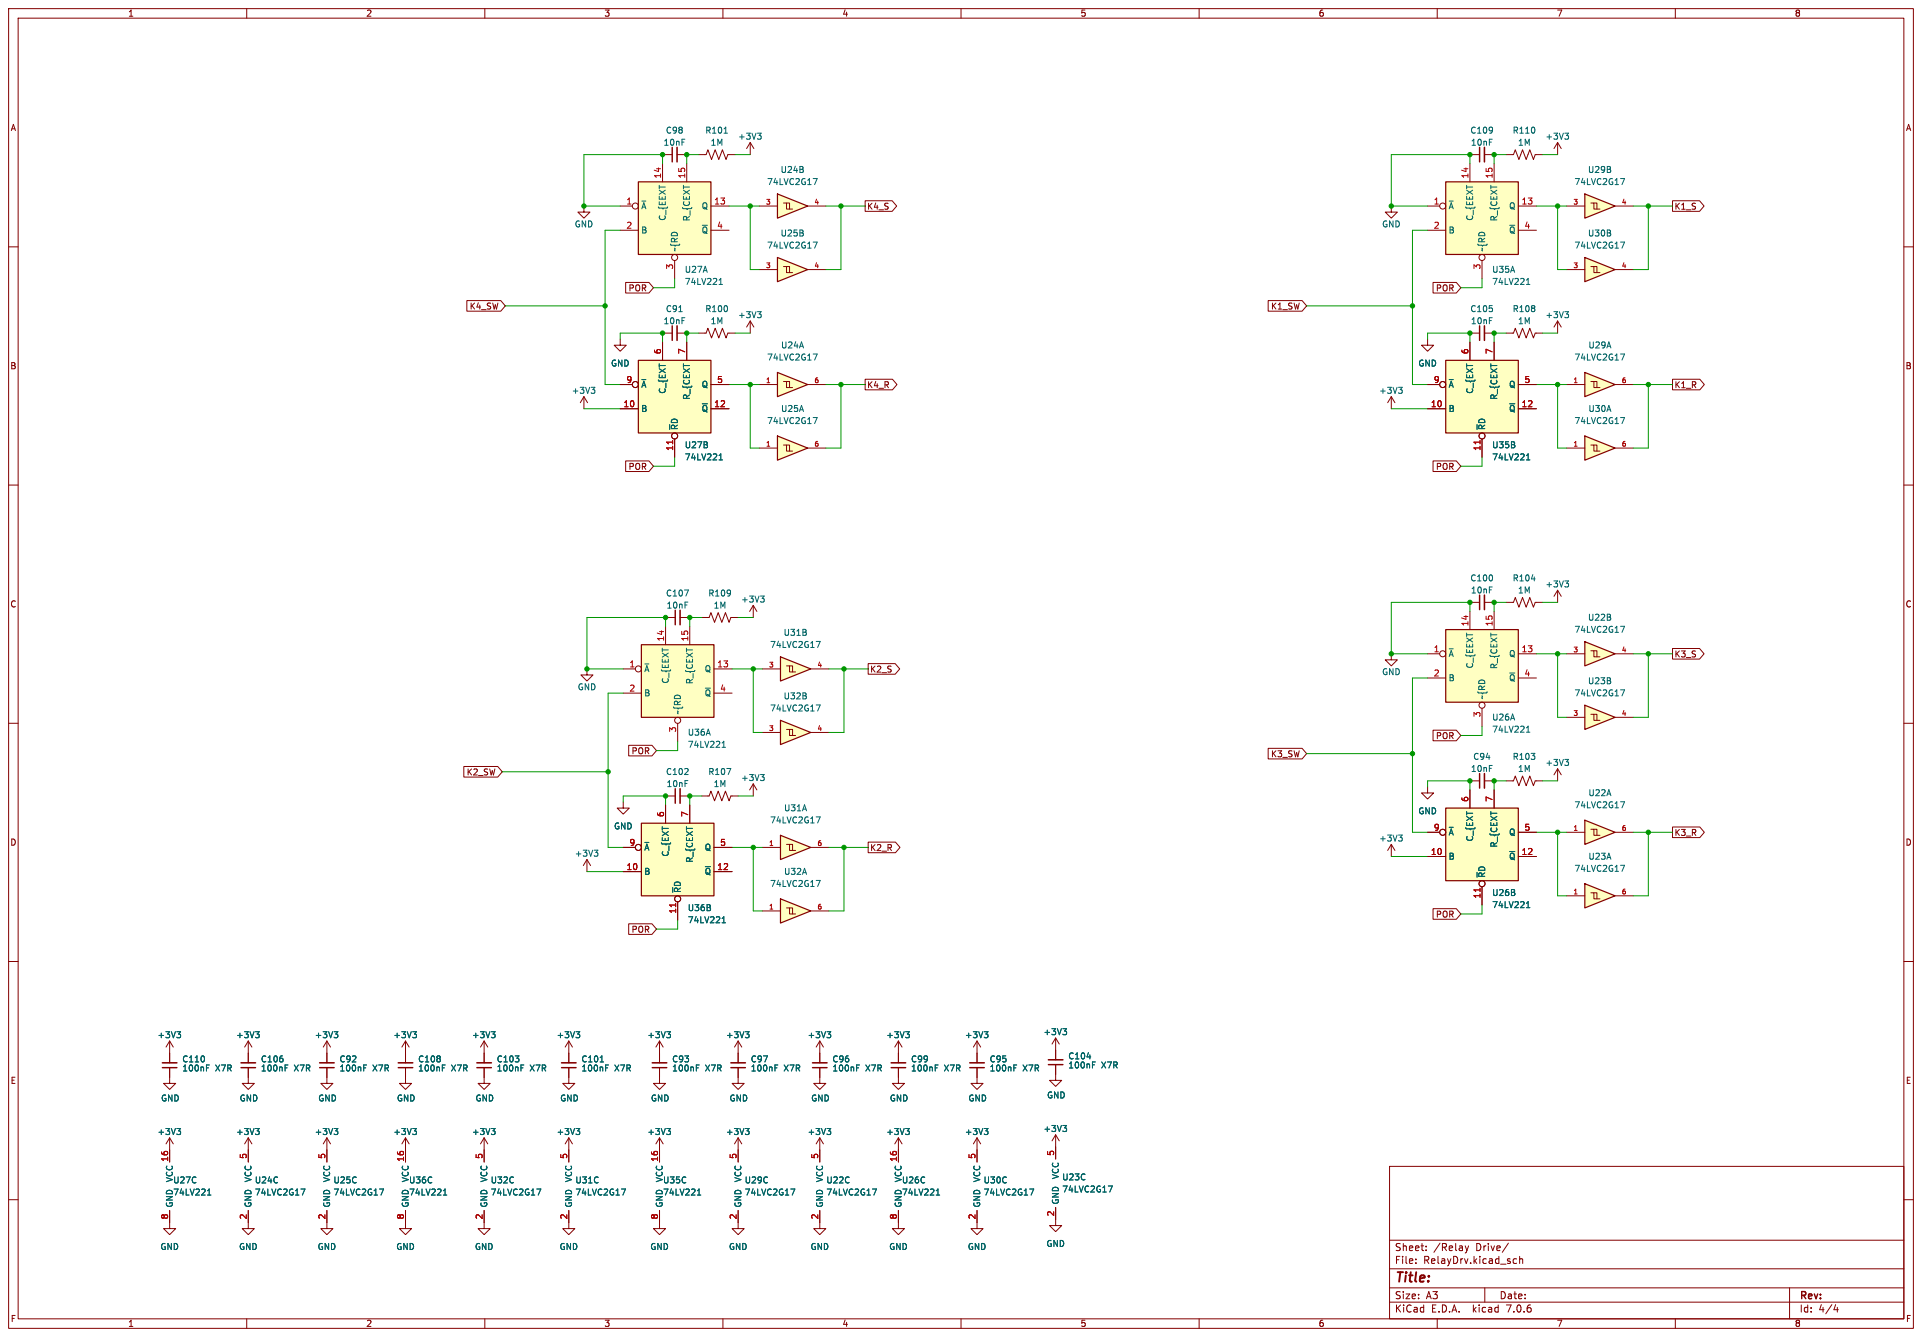
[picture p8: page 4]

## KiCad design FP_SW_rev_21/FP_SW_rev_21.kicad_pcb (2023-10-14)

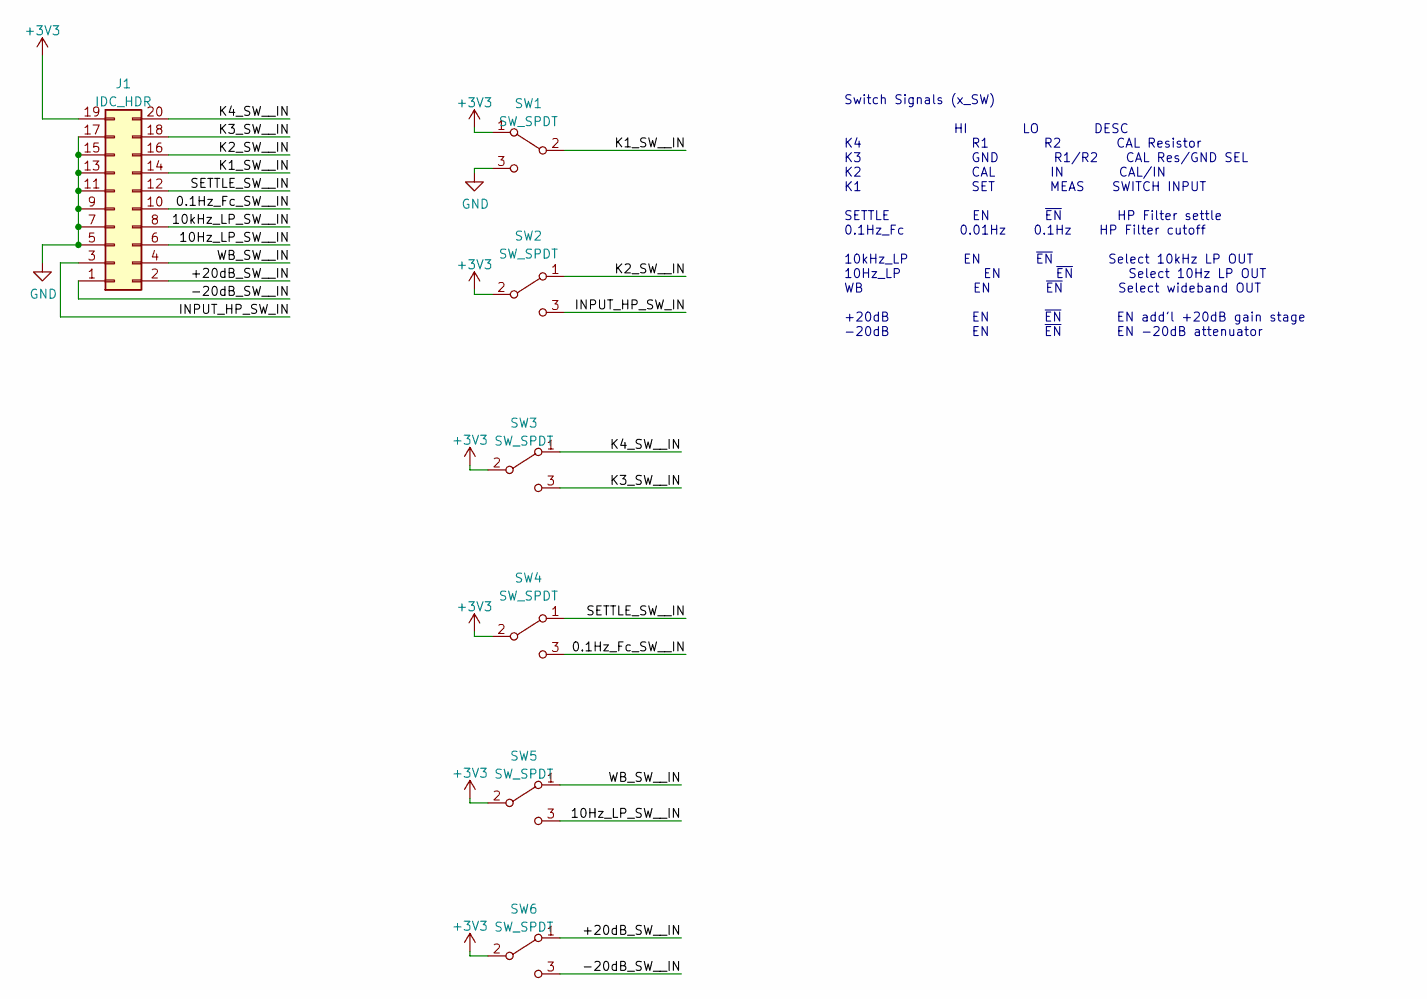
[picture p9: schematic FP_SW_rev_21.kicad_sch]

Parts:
J1: IDC_HDR; PinHeader_2x10_P1.27mm_Vertical
SW1, SW2, SW3, SW4, SW5, SW6: SW_SPDT; SW_SPDT_4.7_mm

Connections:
+3V3: J1.19, SW1.1 (A), SW2.2 (B), SW3.2 (B), SW4.2 (B), SW5.2 (B), SW6.2 (B)
/0.1Hz_Fc_SW__IN: J1.10, SW4.3 (C)
/10Hz_LP_SW__IN: J1.6, SW5.3 (C)
/10kHz_LP_SW__IN: J1.8
/+20dB_SW__IN: J1.2, SW6.1 (A)
/-20dB_SW__IN: J1.1, SW6.3 (C)
/INPUT_HP_SW_IN: J1.3, SW2.3 (C)
/K1_SW__IN: J1.14, SW1.2 (B)
/K2_SW__IN: J1.16, SW2.1 (A)
/K3_SW__IN: J1.18, SW3.3 (C)
/K4_SW__IN: J1.20, SW3.1 (A)
/SETTLE_SW__IN: J1.12, SW4.1 (A)
/WB_SW__IN: J1.4, SW5.1 (A)
GND: J1.5, J1.7, J1.9, J1.11, J1.13, J1.15, J1.17, SW1.3 (C)

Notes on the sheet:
Switch Signals (x_SW) HI LO DESC K4 R1 R2 CAL Resistor K3 GND R1/R2 CAL Res/GND SEL K2 CAL IN CAL/IN K1 SET MEAS SWITCH INPUT SETTLE EN ~{EN} HP Filter settle 0.1Hz_Fc 0.01Hz 0.1Hz HP Filter cutoff 10kHz_LP EN ~{EN} Select 10kHz LP OUT 10Hz_LP EN ~{EN} Select 10Hz LP OUT WB EN ~{EN} Select wideband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

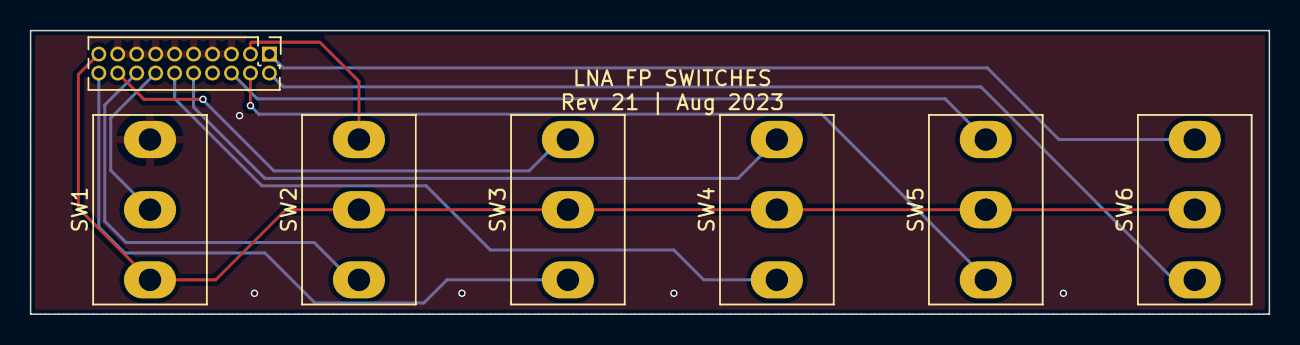
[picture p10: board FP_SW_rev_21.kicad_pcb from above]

Board: 2 copper layers, 83.0 x 19.0 mm, 7 parts (0 on the bottom side), 13 nets.

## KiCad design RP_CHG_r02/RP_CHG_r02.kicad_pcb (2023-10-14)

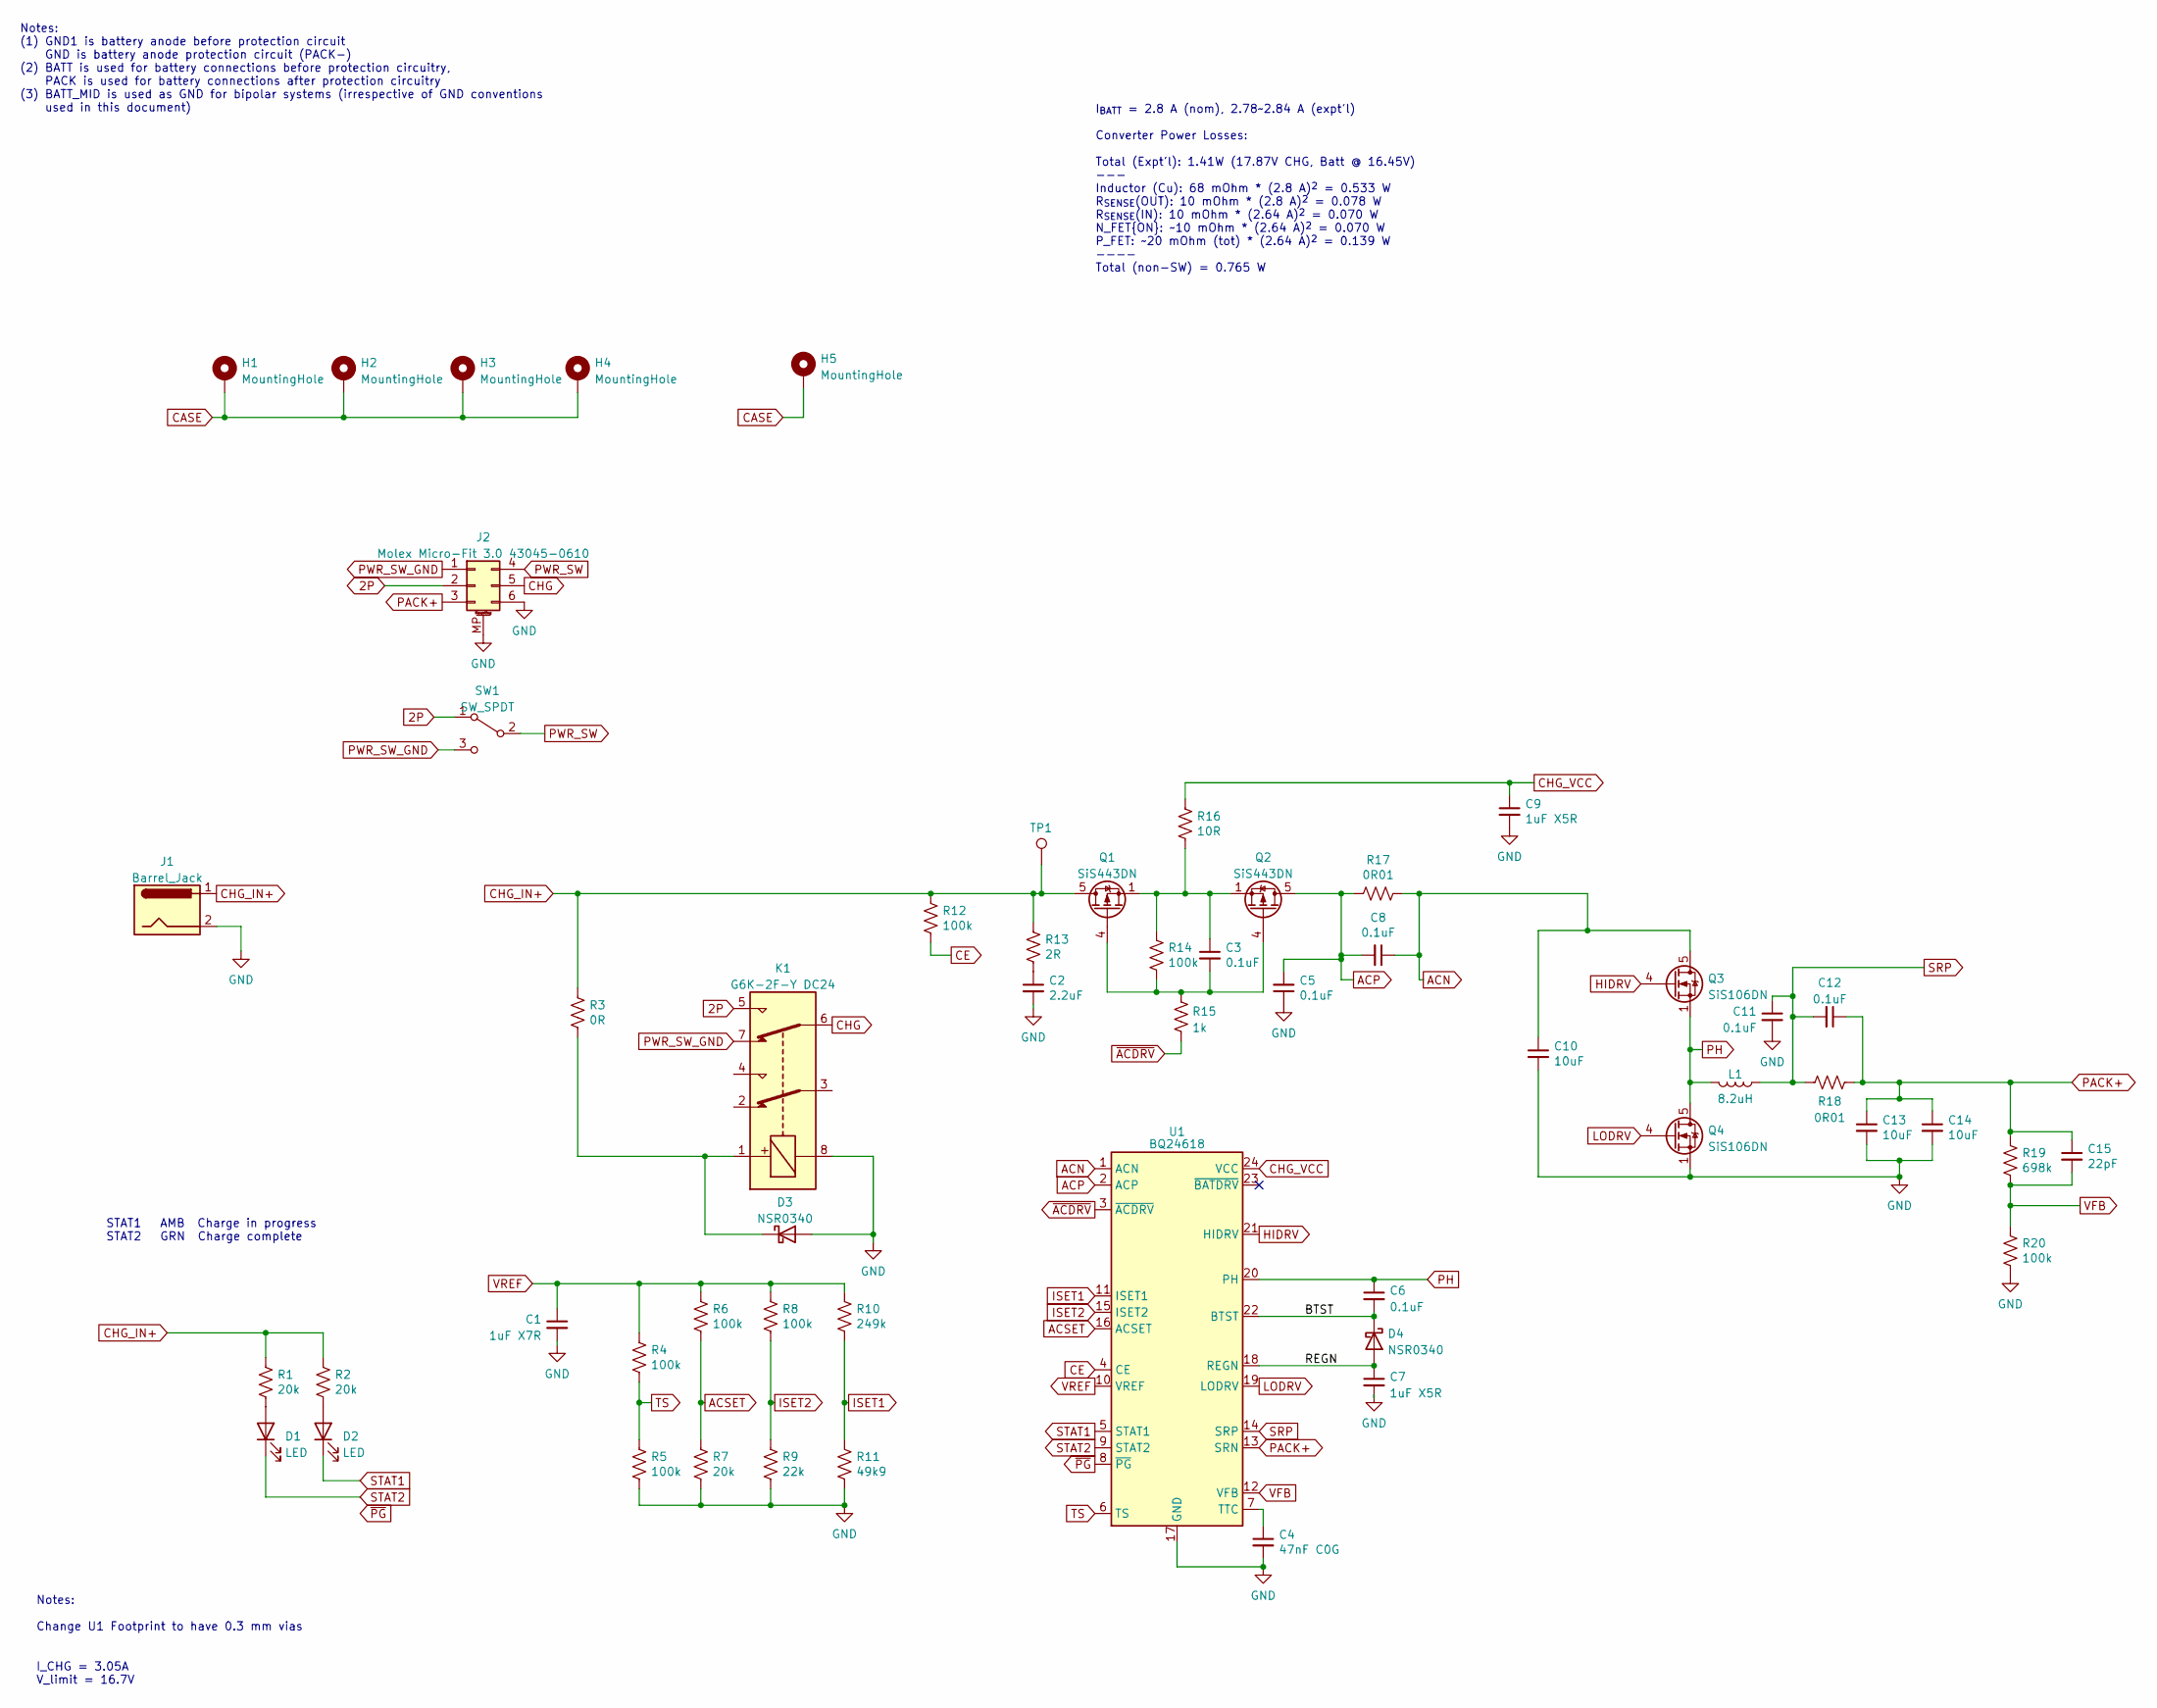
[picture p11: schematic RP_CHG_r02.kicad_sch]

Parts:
C1: 1uF X7R; C_0603_1608Metric_red_outline
C2: 2.2uF; C_1206_3216Metric_Red
C3, C5, C6, C8, C11, C12: 0.1uF; C_0402_1005Metric
C4: 47nF C0G; C_0805_2012Metric_Red_outline
C7, C9: 1uF X5R; C_0402_1005Metric
C10: 10uF; C_1210_3225Metric
C13, C14: 10uF; C_1206_3216Metric_Red
C15: 22pF; C_0603_1608Metric_red_outline
D1, D2: LED; LED_Osram_Lx_P47F_D2mm_ReverseMount
D3, D4: NSR0340; D_SOD-523
H1, H2, H3, H4: MountingHole; MountingHole_4.3mm_M4_ISO14580_Pad
H5: MountingHole; PanelCutout_6.5mm_PTH
J1: Barrel_Jack; BarrelJackDC_Switchcraft721_712
J2: Molex Micro-Fit 3.0 43045-0610; Molex_Micro-Fit_3.0_43045-0610_2x03-1MP_P3.00mm_Horizontal
K1: G6K-2F-Y DC24; Relay_DPDT_Omron_G6K-2F-Y
L1: 8.2uH; L_Vishay_IHLP-2525
Q1, Q2: SiS443DN; Vishay_PowerPAK_1212-8_Single
Q3, Q4: SiS106DN; Vishay_PowerPAK_1212-8_Single
R1, R2, R7: 20k; R_0402_1005Metric
R3: 0R; R_0603_1608Metric_red
R4, R5, R6, R8, R12, R14, R20: 100k; R_0402_1005Metric
R9: 22k; R_0402_1005Metric
R10: 249k; R_0402_1005Metric
R11: 49k9; R_0402_1005Metric
R13: 2R; R_0603_1608Metric_red
R15: 1k; R_0402_1005Metric
R16: 10R; R_0603_1608Metric_red
R17, R18: 0R01; R_1206_3216Metric
R19: 698k; R_0402_1005Metric
SW1: SW_SPDT; TestPoint_3Pads
TP1: TestPoint; TestPoint_Pad_D1.0mm
U1: BQ24618; HVQFN-24-1EP_4x4mm_P0.5mm_EP2.5x2.5mm

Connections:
2P: J2.2, K1.5, SW1.1 (A)
/BTST: C6.2, D4.1 (K), U1.22 (BTST)
/REGN: C7.1, D4.2 (A), U1.18 (REGN)
ACN: C8.1, C10.1, Q3.5 (D), R17.1, U1.1 (ACN)
ACP: C5.2, C8.2, Q2.5 (D), R17.2, U1.2 (ACP)
ACSET: R6.2, R7.1, U1.16 (ACSET)
CASE: H1.1, H2.1, H3.1, H4.1, H5.1
CE: R12.2, U1.4 (CE)
CHG: J2.5, K1.6
CHG_IN+: J1.1, Q1.5 (D), R1.1, R2.1, R3.2, R12.1, R13.1, TP1.1
CHG_VCC: C9.1, R16.2, U1.24 (VCC)
EP: C1.2, C2.2, C4.2, C5.1, C7.2, C9.2, C10.2, C11.2, C13.2, C14.2, D3.2 (A), J1.2, J2.6, J2.MP (MountPin), K1.8, Q4.1 (S), Q4.2 (S), Q4.3 (S), R5.2, R7.2, R9.2, R11.2, R20.1, U1.17 (GND), U1.25 (EP)
HIDRV: Q3.4 (G), U1.21 (HIDRV)
ISET1: R10.2, R11.1, U1.11 (ISET1)
ISET2: R8.2, R9.1, U1.15 (ISET2)
LODRV: Q4.4 (G), U1.19 (LODRV)
unnamed: C2.1, R13.2
unnamed: C3.1, Q1.1 (S), Q1.2 (S), Q1.3 (S), Q2.1 (S), Q2.2 (S), Q2.3 (S), R14.1, R16.1
unnamed: C3.2, Q1.4 (G), Q2.4 (G), R14.2, R15.1
unnamed: C4.1, U1.7 (TTC)
unnamed: D1.2 (A), R1.2
unnamed: D2.2 (A), R2.2
unnamed: D3.1 (K), K1.1, R3.1
PACK+: C12.1, C13.1, C14.1, C15.1, J2.3, R18.1, R19.2, U1.13 (SRN)
PH: C6.1, L1.2, Q3.1 (S), Q3.2 (S), Q3.3 (S), Q4.5 (D), U1.20 (PH)
PWR_SW: J2.4, SW1.2 (B)
PWR_SW_GND: J2.1, K1.7, SW1.3 (C)
SRP: C11.1, C12.2, L1.1, R18.2, U1.14 (SRP)
STAT1: D2.1 (K), U1.5 (STAT1)
STAT2: D1.1 (K), U1.9 (STAT2)
TS: R4.2, R5.1, U1.6 (TS)
VFB: C15.2, R19.1, R20.2, U1.12 (VFB)
VREF: C1.1, R4.1, R6.1, R8.1, R10.1, U1.10 (VREF)
~ACDRV: R15.2, U1.3 (~ACDRV)
~PG: U1.8 (~PG)

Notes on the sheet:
I_{BATT} = 2.8 A (nom), 2.78~2.84 A (expt'l) Converter Power Losses: Total (Expt'l): 1.41W (17.87V CHG, Batt @ 16.45V) --- Inductor (Cu): 68 mOhm * (2.8 A)^{2} = 0.533 W R_{SENSE}(OUT): 10 mOhm * (2.8 A)^{2} = 0.078 W R_{SENSE}(IN): 10 mOhm * (2.64 A)^{2} = 0.070 W N_FET{ON}: ~10 mOhm * (2.64 A)^{2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
I_CHG = 3.05A V_limit = 16.7V
Notes: (1) GND1 is battery anode before protection circuit GND is battery anode protection circuit (PACK-) (2) BATT is used for battery connections before protection circuitry, PACK is used for battery connections after protection circuitry (3) BATT_MID is used as GND for bipolar systems (irrespect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
STAT1 AMB Charge in progress STAT2 GRN Charge complete
Notes: Change U1 Footprint to have 0.3 mm vias

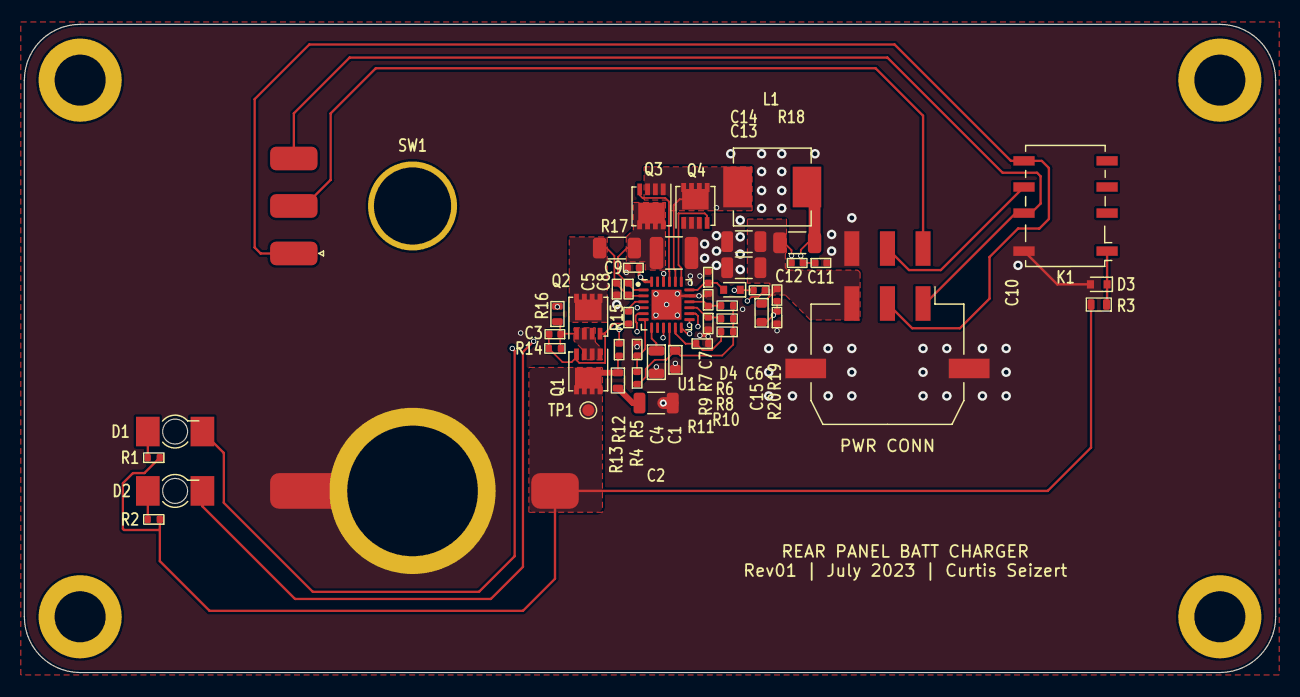
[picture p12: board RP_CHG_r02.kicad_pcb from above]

Board: 4 copper layers, 105.4 x 54.6 mm, 55 parts (0 on the bottom side), 34 nets.

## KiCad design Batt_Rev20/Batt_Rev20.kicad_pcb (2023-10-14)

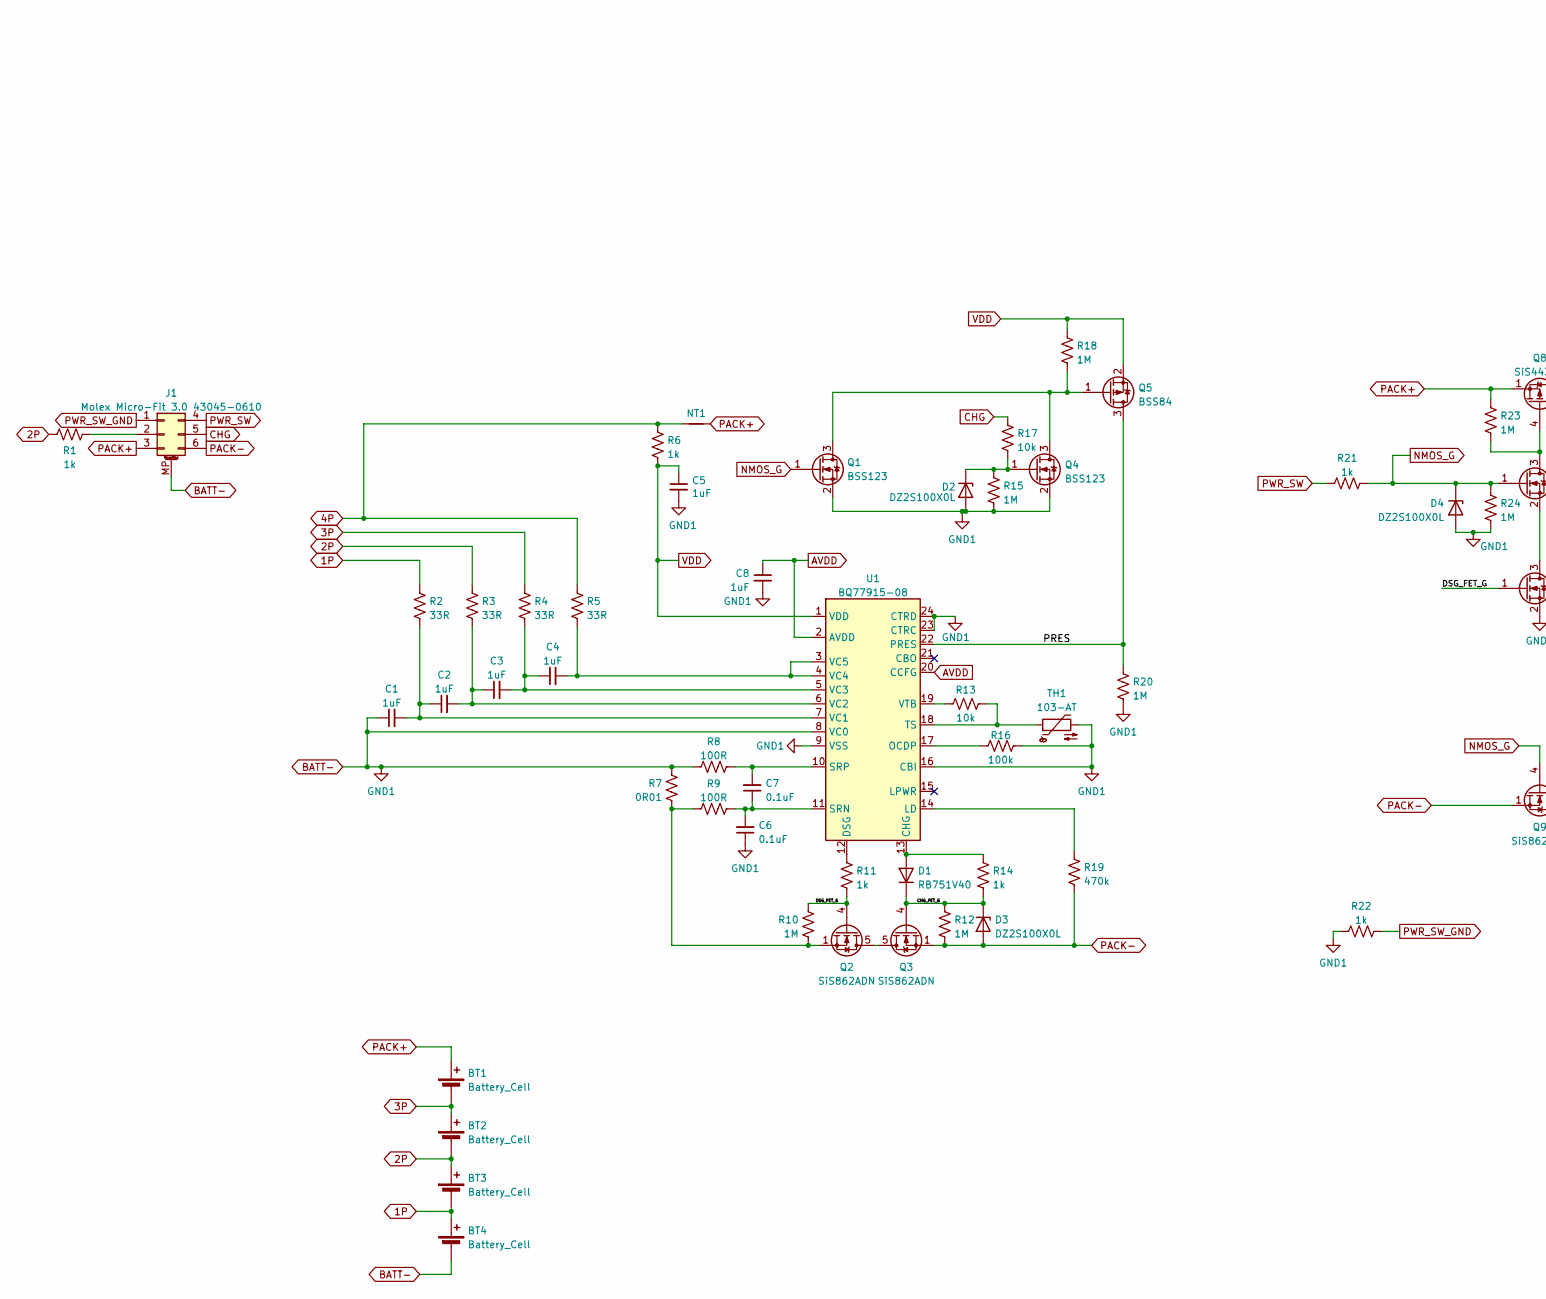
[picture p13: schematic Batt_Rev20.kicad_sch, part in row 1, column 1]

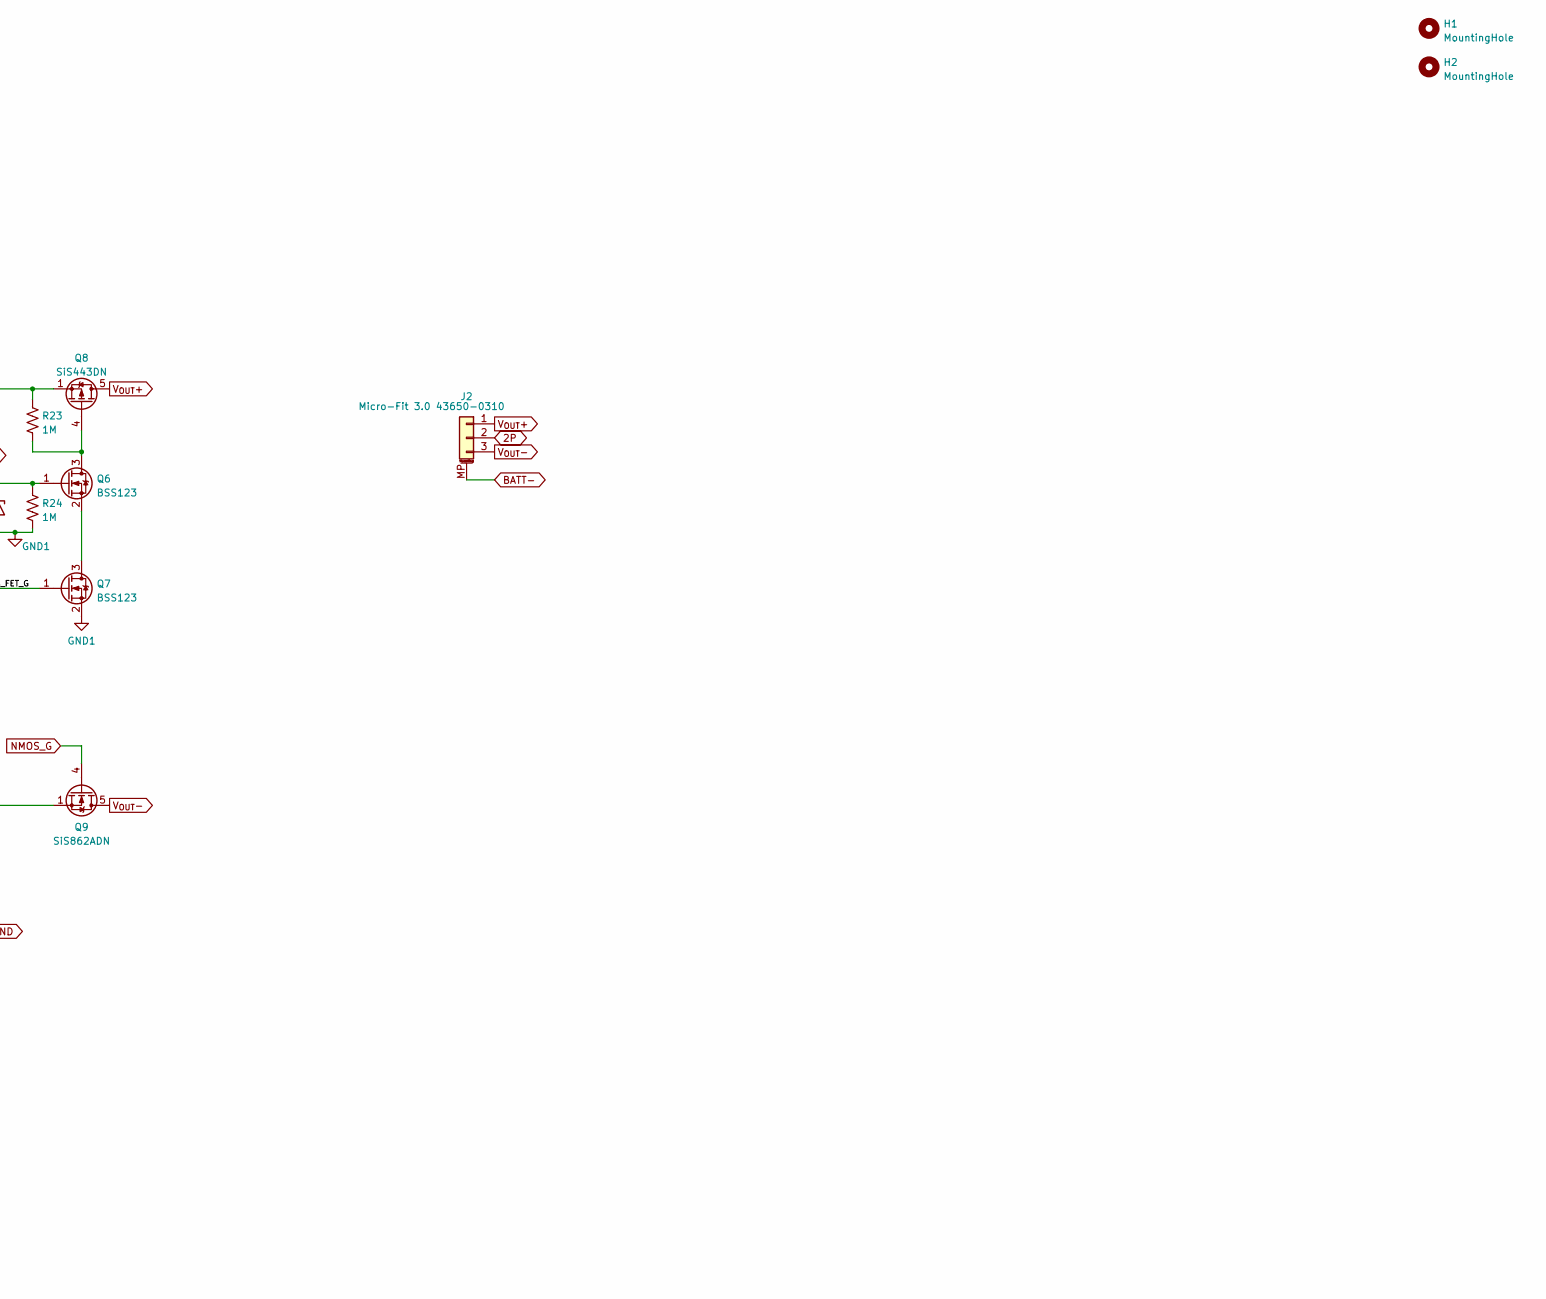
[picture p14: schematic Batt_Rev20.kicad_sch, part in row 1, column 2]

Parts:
BT1, BT2, BT3, BT4: Battery_Cell; BatteryHolder_Keystone246_21700
C1, C2, C3, C4, C5, C8: 1uF; C_0603_1608Metric_red_outline
C6, C7: 0.1uF; C_0603_1608Metric_red_outline
D1: RB751V40; D_SOD-323
D2, D3, D4: DZ2S100X0L; D_SOD-523
H1, H2: MountingHole; MountingHole_3.2mm_M3_Pad_Via
J1: Molex Micro-Fit 3.0 43045-0610; Molex_Micro-Fit_3.0_43045-0610_2x03-1MP_P3.00mm_Horizontal
J2: Micro-Fit 3.0 43650-0310; Molex_Micro-Fit_3.0_43650-0310_1x03-1MP_P3.00mm_Horizontal
NT1: Net-Tie_2; NetTie-2_SMD_Pad0.2mm
Q1, Q4, Q6, Q7: BSS123; SOT-23
Q2, Q3, Q9: SiS862ADN; Vishay_PowerPAK_1212-8_Single
Q5: BSS84; SOT-23
Q8: SiS443DN; Vishay_PowerPAK_1212-8_Single
R1, R6, R11, R14, R21, R22: 1k; R_0603_1608Metric_red
R2, R3, R4, R5: 33R; R_0603_1608Metric_red
R7: 0R01; R_1206_3216Metric_red
R8, R9: 100R; R_0603_1608Metric_red
R10, R12, R15, R18, R20, R23, R24: 1M; R_0603_1608Metric_red
R13, R17: 10k; R_0603_1608Metric_red
R16: 100k; R_0603_1608Metric_red
R19: 470k; R_0603_1608Metric_red
TH1: 103-AT; R_0603_1608Metric
U1: BQ77915-08; TSSOP-24_4.4x7.8mm_P0.65mm

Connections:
1P: BT3.1 (-), BT4.2 (+), R2.1
2P: BT2.1 (-), BT3.2 (+), J2.2, R1.1, R3.1
3P: BT1.1 (-), BT2.2 (+), R4.1
4P: NT1.2, R5.1, R6.1
/CHG_FET_G: D1.1 (K), D3.1 (K), Q3.4 (G), R12.1, R14.2
/DSG_FET_G: Q2.4 (G), Q7.1 (G), R10.1, R11.2
/PRES: Q5.3 (D), R20.1, U1.22 (PRES)
AVDD: C8.1, U1.2 (AVDD), U1.20 (CCFG)
BATT-: BT4.1 (-), C1.1, C5.2, C6.1, C8.2, D2.2 (A), D4.2 (A), J1.MP (MountPin), J2.MP (MountPin), Q1.2 (S), Q4.2 (S), Q7.2 (S), R7.1, R8.1, R15.2, R16.1, R20.2, R22.1, R24.2, TH1.2, U1.8 (VC0), U1.9 (VSS), U1.16 (CBI), U1.23 (CTRC), U1.24 (CTRD)
CHG: J1.5, R17.1
NMOS_G: D4.1 (K), Q1.1 (G), Q6.1 (G), Q9.4 (G), R21.2, R24.1
unnamed: C1.2, C2.1, R2.2, U1.7 (VC1)
unnamed: C2.2, C3.1, R3.2, U1.6 (VC2)
unnamed: C3.2, C4.1, R4.2, U1.5 (VC3)
unnamed: C4.2, R5.2, U1.3 (VC5), U1.4 (VC4)
unnamed: C6.2, C7.1, R9.1, U1.11 (SRN)
unnamed: C7.2, R8.2, U1.10 (SRP)
unnamed: D1.2 (A), R14.1, U1.13 (CHG)
unnamed: D2.1 (K), Q4.1 (G), R15.1, R17.2
unnamed: Q2.1 (S), Q2.2 (S), Q2.3 (S), R7.2, R9.2, R10.2
unnamed: Q2.5 (D), Q3.5 (D)
unnamed: Q1.3 (D), Q4.3 (D), Q5.1 (G), R18.2
unnamed: Q6.3 (D), Q8.4 (G), R23.2
unnamed: Q6.2 (S), Q7.3 (D)
unnamed: J1.2, R1.2
unnamed: R11.1, U1.12 (DSG)
unnamed: R13.1, TH1.1, U1.18 (TS)
unnamed: R13.2, U1.19 (VTB)
unnamed: R16.2, U1.17 (OCDP)
unnamed: R19.1, U1.14 (LD)
PACK+: BT1.2 (+), J1.3, NT1.1, Q8.1 (S), Q8.2 (S), Q8.3 (S), R23.1
PACK-: D3.2 (A), J1.6, Q3.1 (S), Q3.2 (S), Q3.3 (S), Q9.1 (S), Q9.2 (S), Q9.3 (S), R12.2, R19.2
PWR_SW: J1.4, R21.1
PWR_SW_GND: J1.1, R22.2
VDD: C5.1, Q5.2 (S), R6.2, R18.1, U1.1 (VDD)
V_{OUT}+: J2.1, Q8.5 (D)
V_{OUT}-: J2.3, Q9.5 (D)

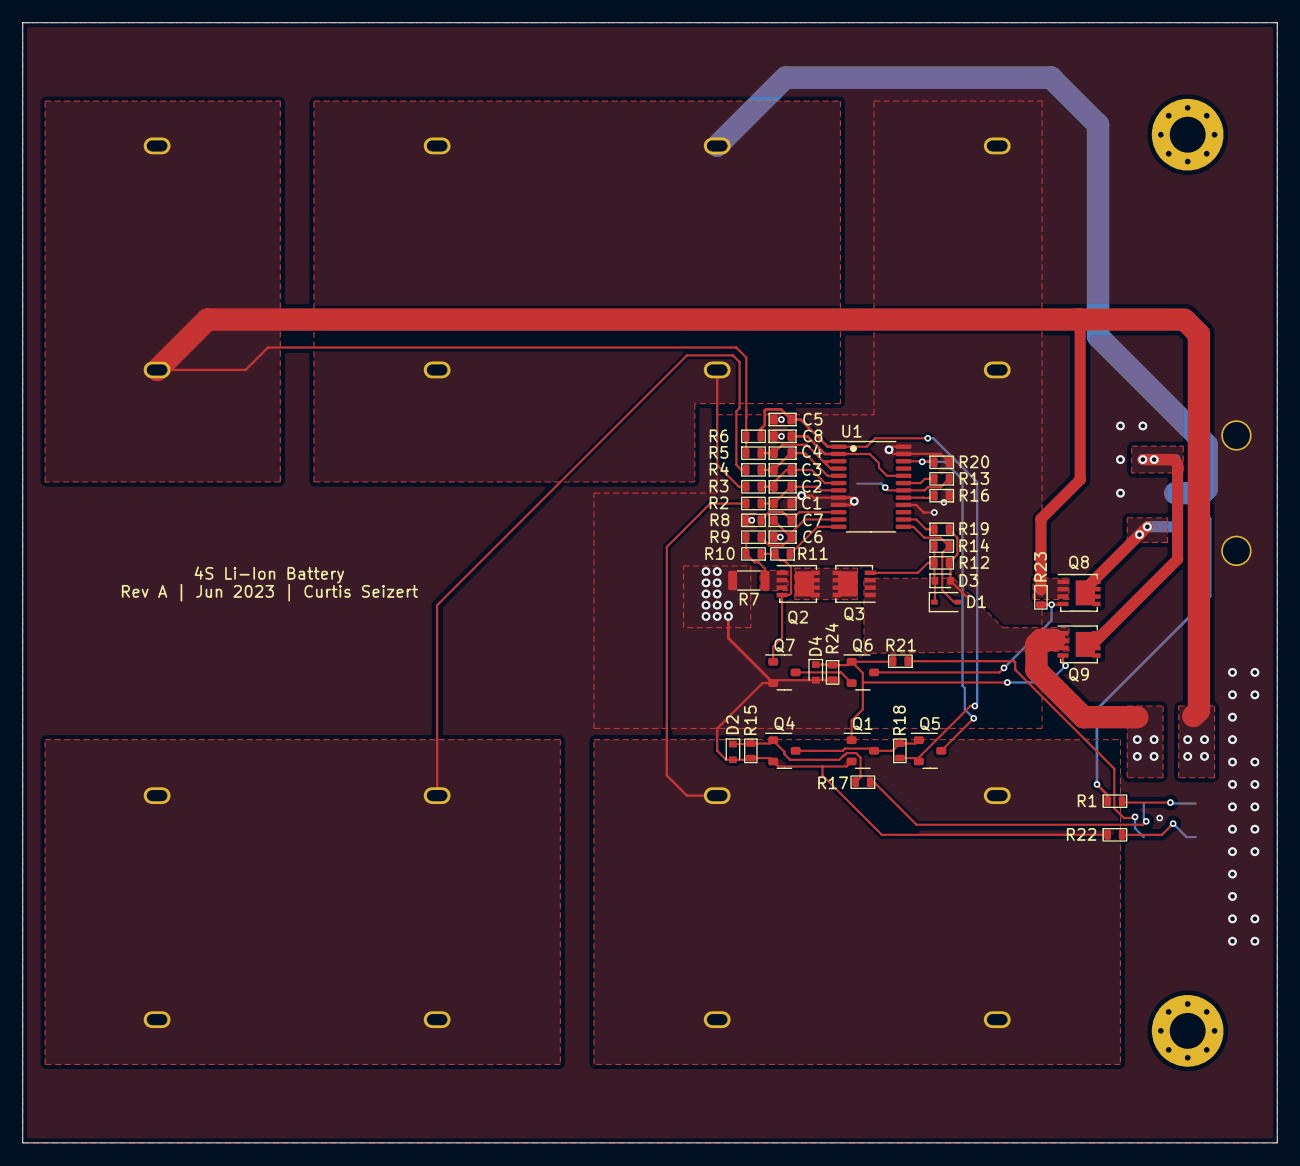
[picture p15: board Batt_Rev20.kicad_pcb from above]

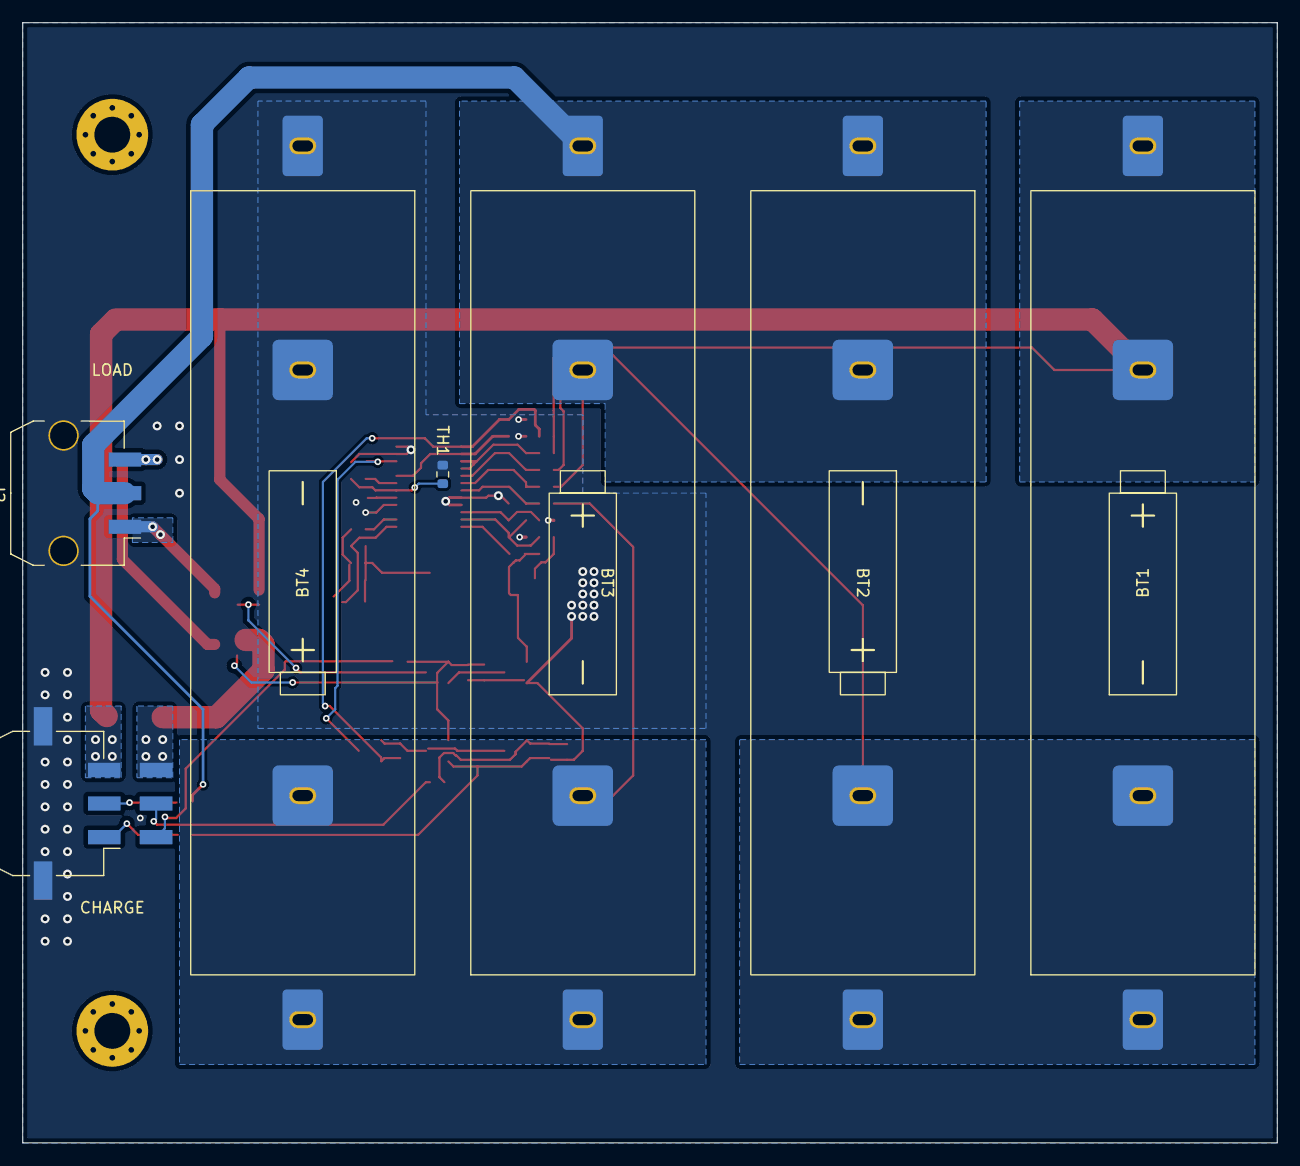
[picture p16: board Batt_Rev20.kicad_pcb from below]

Board: 2 copper layers, 112.0 x 100.0 mm, 56 parts (7 on the bottom side), 37 nets.

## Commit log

2023-10-14 Second Commit
    [FP_SW_rev_21-B_Cu.gbl, FP_SW_rev_21-B_Mask.gbs, FP_SW_rev_21-B_Paste.gbp, FP_SW_rev_21-B_Silkscreen.gbo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]
2023-11-09 Update README.md
    Added current status and issues sections, updated electrical characteristics with more extensive testing.
